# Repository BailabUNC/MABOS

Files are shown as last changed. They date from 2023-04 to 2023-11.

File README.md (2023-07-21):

# MABOS
*All work in the MABOS repository is under Copyright Protections enumerated in the LICENSE file. Please contact Arjun Putcha - arjun22@live.unc.edu - for any questions related to redistribution of this work*

*Please see [fastplotlib](https://github.com/kushalkolar/fastplotlib/tree/master), developed by Kushal Kolar, to learn more about the plotting library we primarily use.

https://github.com/BailabUNC/MABOS/assets/96029511/e3c2583f-f5fd-4558-a8c5-83fa992f67cb

There are three key folders in this repository: full_design, firmware, and application.

## Full Design
This folder contains the *CAD* files (.sch and .brd) detailing schematic and layout of our pulse oximeter. It also contains a CAD library file - COMPONENTS_LIB.flbr - that has the relevant files for each component used in our design.

There is also a folder *Fab_Outputs* that contains the fabrication files necessary for laser cutting the top and bottom side of the board. *_autocad.dxf* files contain the file compatible with our laser cutter. Refer to *protocols/PCB_protocols.pdf* to follow our fabrication process.

Below is the schematic for our Infrared LED and Photodiode drivers; The 5-stage analog signal processing pipeline and led drivers are detailed in the schematic. The same schematic is used for the two other channels.
MABOS Schematic

## Firmware
There are 3 directories in this folder: Arduino, Python, and zephyr_workspace.

### Arduino
Contains the .ino file used for the adafruit_itsybitsy_nrf52840 board. The code allows for the control of 3 LED channels and 3 ADC channels. Currently, the duty cycle is set to 50%, and the acquisition rate at 100 Hz.

We also take a burst sample of each ADC (currently 5 samples) to mitigate some noise, and implement a moving average filter with a window size of 10 samples to smooth the output data.

### Python
The code here will soon be removed.

### Zephyr Workspace
Contains the source code, build files, and modified board files to use the adafruit_itsybitsy_nrf52840 board. The board files are modified to configure 3 LED and 3 ADC channels. You can reference the readme file in *firmware/zephyr_workspace* for further details on modifications made.

## Application
The *utils* folder contains the core API used to acquire, plot, and save biosensor data in real time. The *PPG Widget* python notebook utilizes the core API to operate our device. When running this script, a file named *cache.sqlite3* will be created that contains all acquired data. For our uses, we've found a minute of data acquisition corresponds to ~1 MB of data saved.

The *GUI* folder contains a QT Desktop application used solely for displaying acquired biometrics, including SpO2, Heart Rate, Respiration Rate, and Epidermal Melanin Concentration.

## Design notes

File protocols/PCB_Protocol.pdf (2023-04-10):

1.) Export circuit design (.brd file in Fusion360) as Gerber Zip File

a.

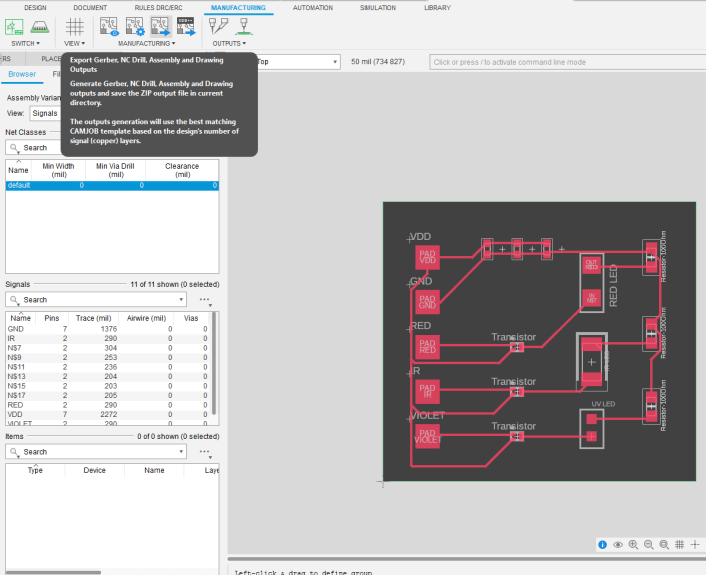
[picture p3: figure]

b. Select “Export Gerber, NC Drill, Assembly, and Drawing Output” output button, and export all files to a .zip file
c. You should see a file named copper_top.gerber in the CAMOutputs folder

i.
2.) Open FlatCAM

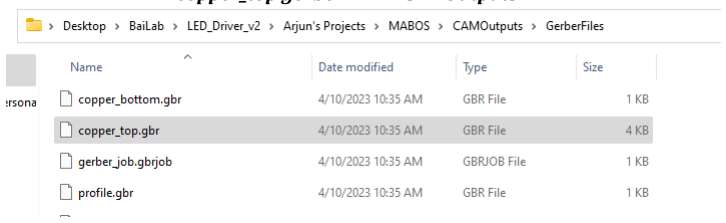
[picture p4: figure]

a. Click ‘File’ and ‘Open Gerber’
b. Navigate to the file you saved above (copper_top.gbr), select said file

c.

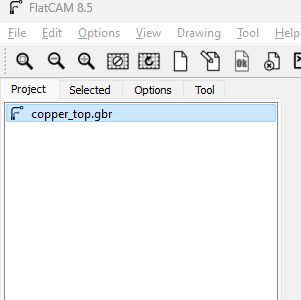
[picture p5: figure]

d. You should see the above file in the project list. Double Click it
e. Modify the parameters as listed below for Total Diameter and Pass Overlap, confirm the resulting design properly traces the counters of each trace be clicking Generate Geometry and visually confirming accuracy, then select File -> Export SVG

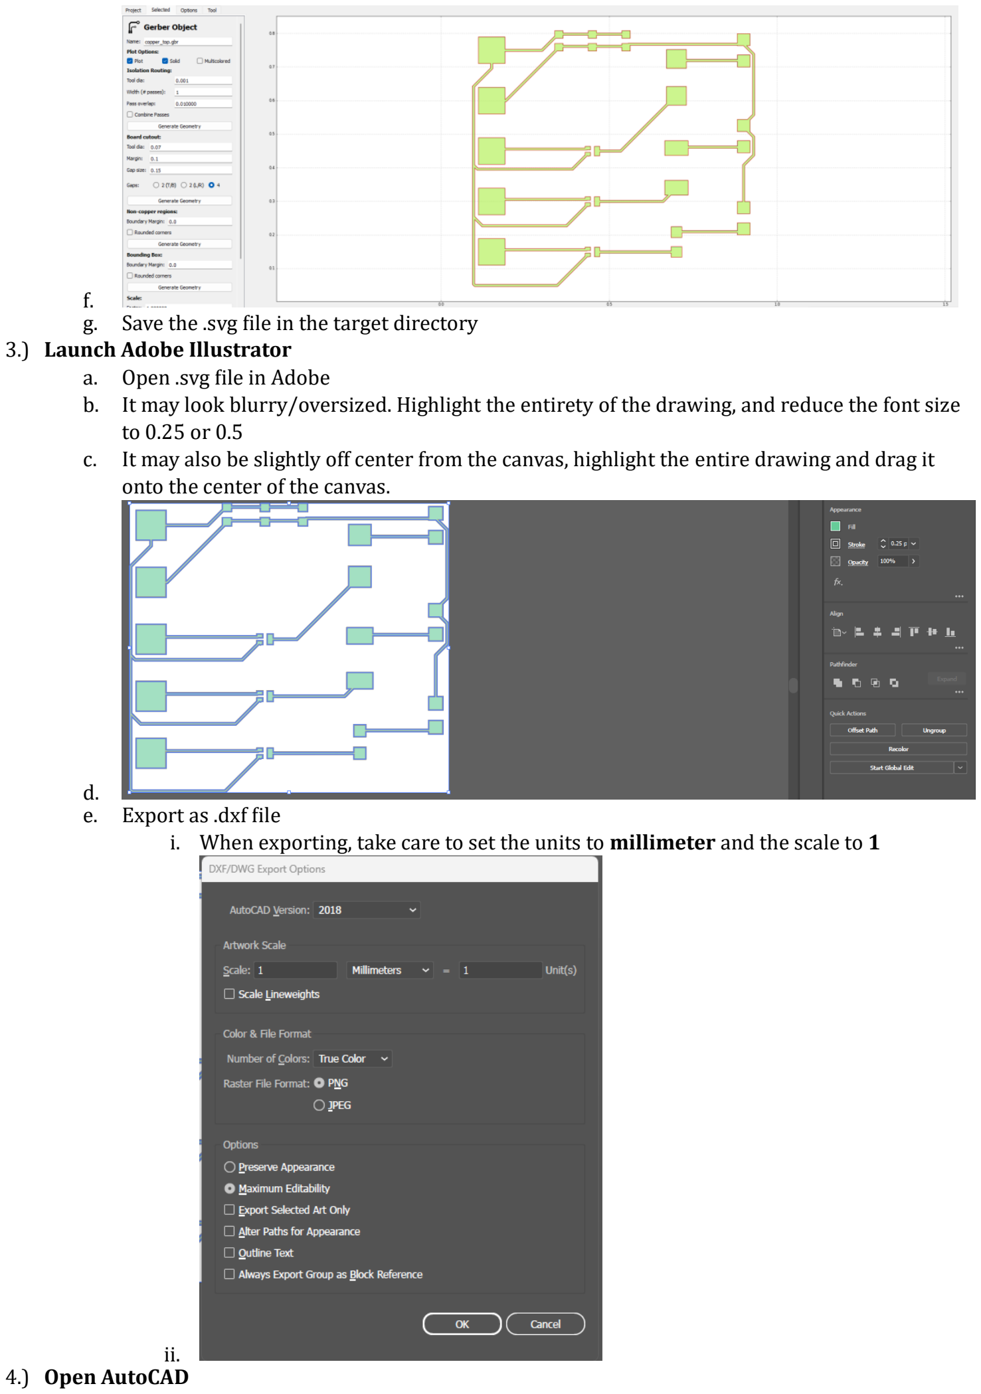
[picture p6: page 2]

f.
g. Save the .svg file in the target directory
3.) Launch Adobe Illustrator
a. Open .svg file in Adobe
b. It may look blurry/oversized. Highlight the entirety of the drawing, and reduce the font size to 0.25 or 0.5
c. It may also be slightly off center from the canvas, highlight the entire drawing and drag it onto the center of the canvas.

d.
e. Export as .dxf file
i. When exporting, take care to set the units to millimeter and the scale to 1

ii.
4.) Open AutoCAD

a. Open the .dxf file

i.

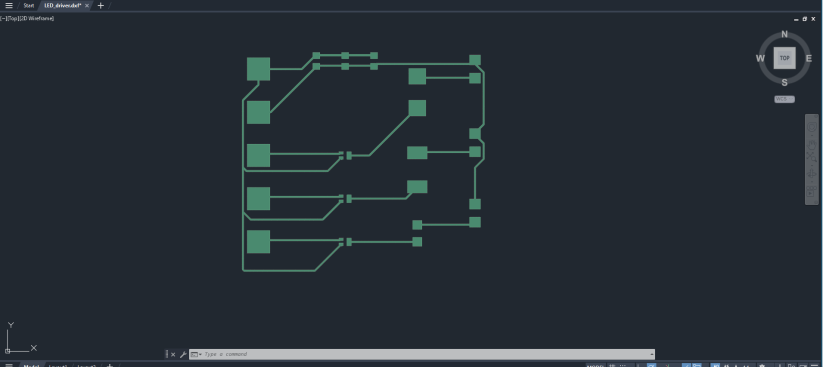
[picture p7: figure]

b. Select the entire circuit, and type X, and you should see the word EXPLODE pop up. Click enter

i.

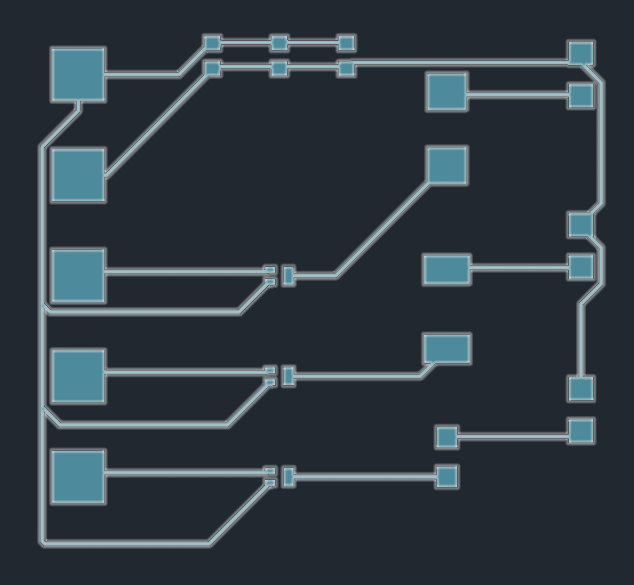
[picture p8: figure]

ii. Repeat this step once more
c. Upon doing step B, you should be able to select individual circuit traces as shown below

i.

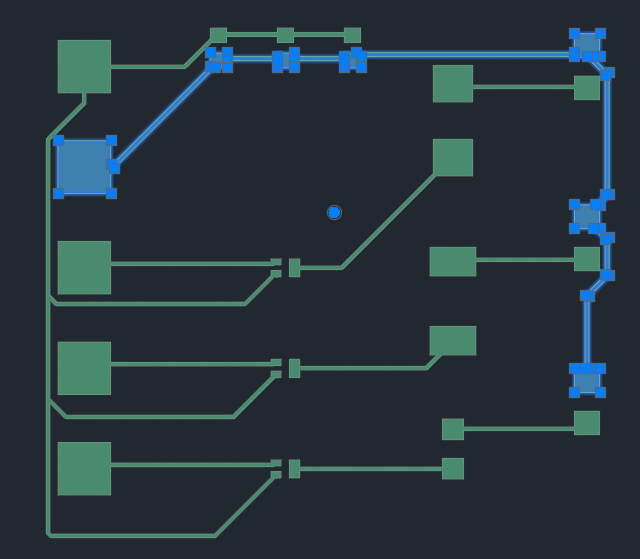
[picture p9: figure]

d. Highlight the entire circuit, type QS and the word Quick Select should pop up. Click enter, the following window will open up:

i.

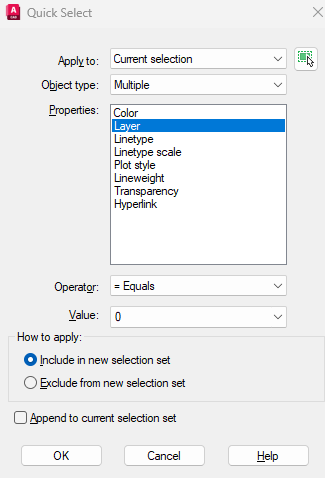
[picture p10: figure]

ii. Set Property to Layer
e. Save the resulting file as a .dxf file, copy this resulting file to a thumbdrive/flashdrive
5.) Launch EZCAD on the desktop associated with the laser printer, plug in the thumbdrive and import the .dxf file
a. File -> Import Vector File -> File_Path.dxf
b. Draw a Rectangle around the entire circuit by selecting Draw Rectangle (yellow square icon on the left vertical bar of the application window).
c. Select the circuit and rectangle elements in the Object List panel, and then click Hatch (the top horizontal bar of the application window, icon looks like an H)
d. Set Hatch Type to the concentric square mode, as shown below, and the Line Space to 0.015, or however small needed to get a good output

e.

f.

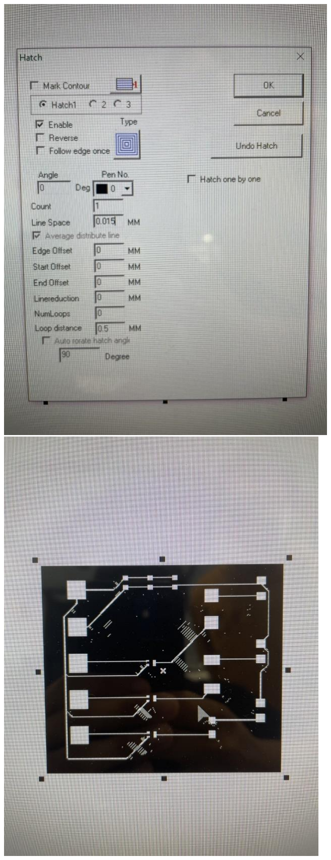
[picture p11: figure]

i. Good output ^
ii. Random ‘shading’ is normal
6.) Laser Cutting Process
a. Take sheet of Copper-FR4, align under the laser.
i. Spray the copper sheet with a thin film of soldermask, dry with pressurized air carefully
b. Make sure the ‘dot’ and ‘line’ of the laser align by adjusting the height of the laser.

c. Select ‘Red’ or ‘Light’ on the bottom of the screen to highlight the area to be cut. Align the copper board appropriately. If you cannot see outline (UV Laser has this issue), place a white tissue above the copper plate. You should now see the outline.
d. Test the settings of the laser
i. For the UV Laser, I used:
1. Loop Count: 1
2. Speed: 1200
3. Current: 0.08
4. Everything else: default ii. For IR Laser, I Used:
1. Power: 30%
2. Loop Count: 1
iii. Cut
7.) Acid Etching
a. Wear PPE
b. Place acid etchant into a rectangular tray, enough to submerge pcb
c. Place pcb within acid using plastic tweezers
d. Start the rocker, leave within for 16 minutes at speed 40
8.) Acetone Wash
a. After acid etching, take pcb out of acid bath using plastic tweezers
b. In a separate, empty, container, use acetone the clean the PCB (hold the pcb with metal tweezers now)
c. Do so until all solder mask has washed off
d. Once done, dispose of all chemicals in chemical waste bin, and clean pcb with water
e. DONE!

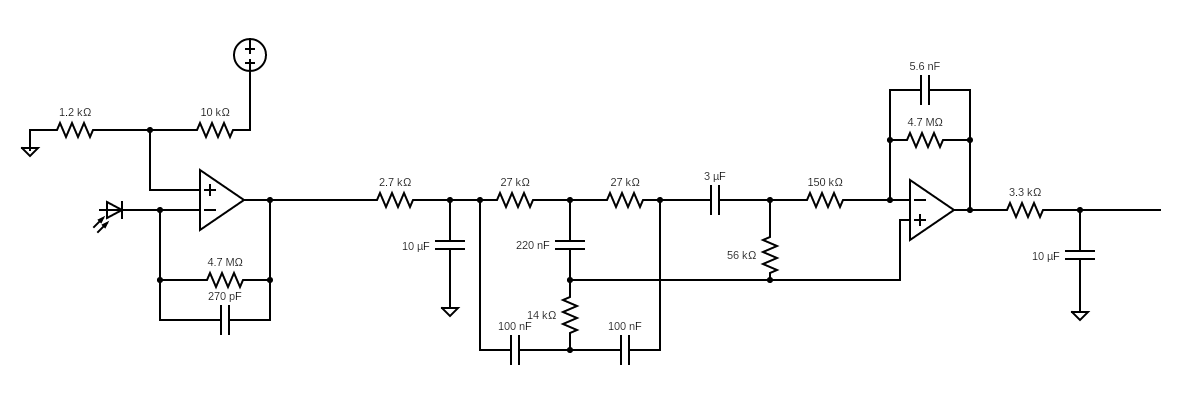
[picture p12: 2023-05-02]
protocols/Filter_Amplification_PD_Schematic.png

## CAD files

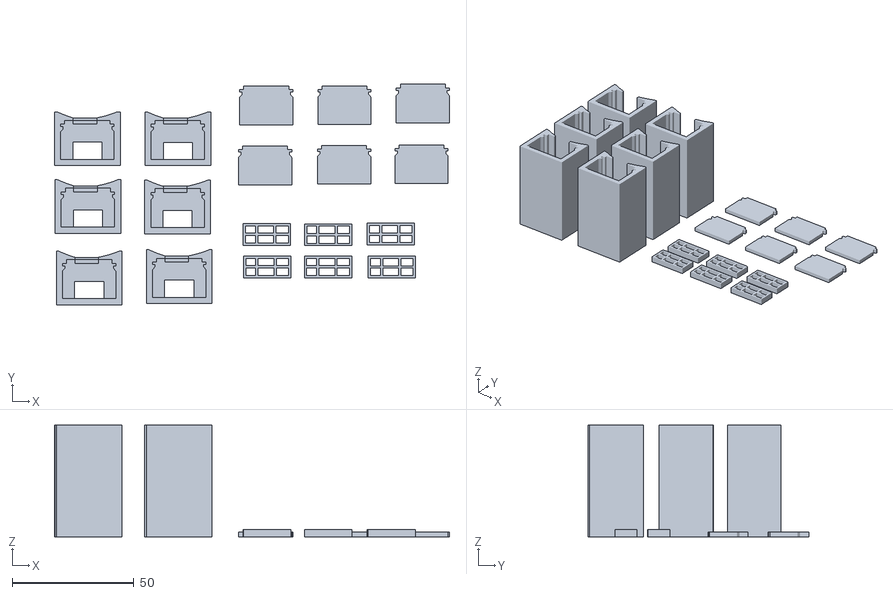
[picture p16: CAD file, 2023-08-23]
full_design/casing/six_full_casings.stl
162.1 x 90.5 x 45.8

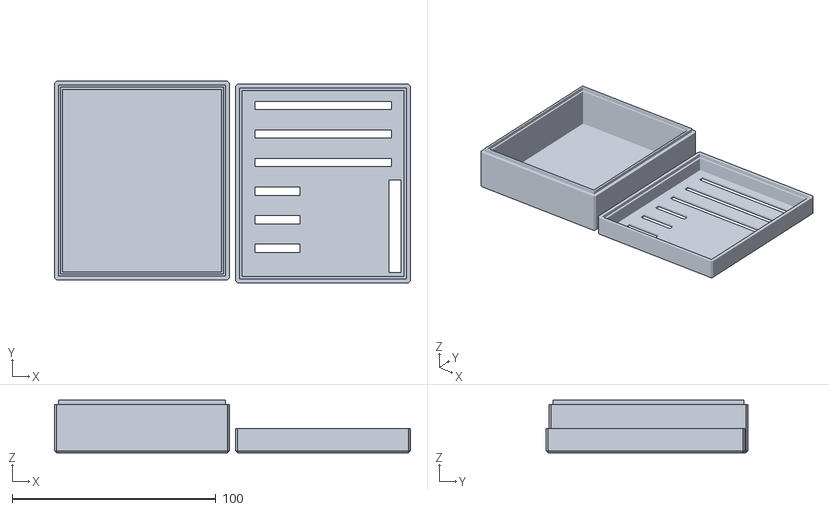
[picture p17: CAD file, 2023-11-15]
full_design/casing/modular_case_design.stl
174.7 x 99.0 x 26.0

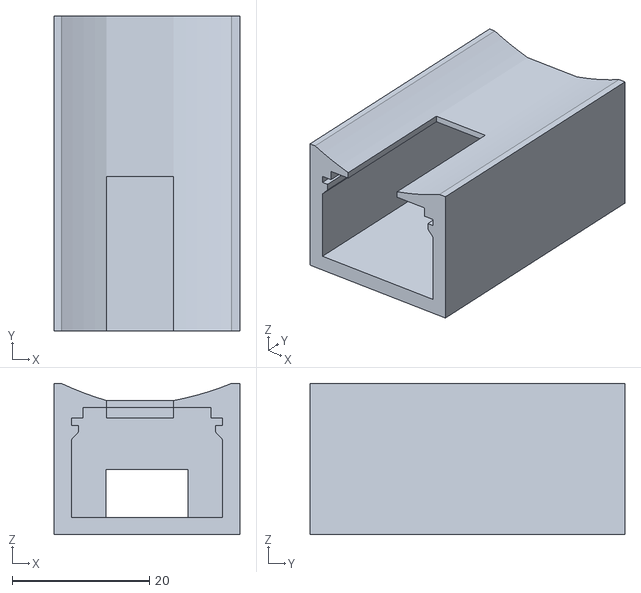
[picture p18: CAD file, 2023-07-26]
full_design/casing/primary_case_design.stl
27.0 x 45.8 x 22.0

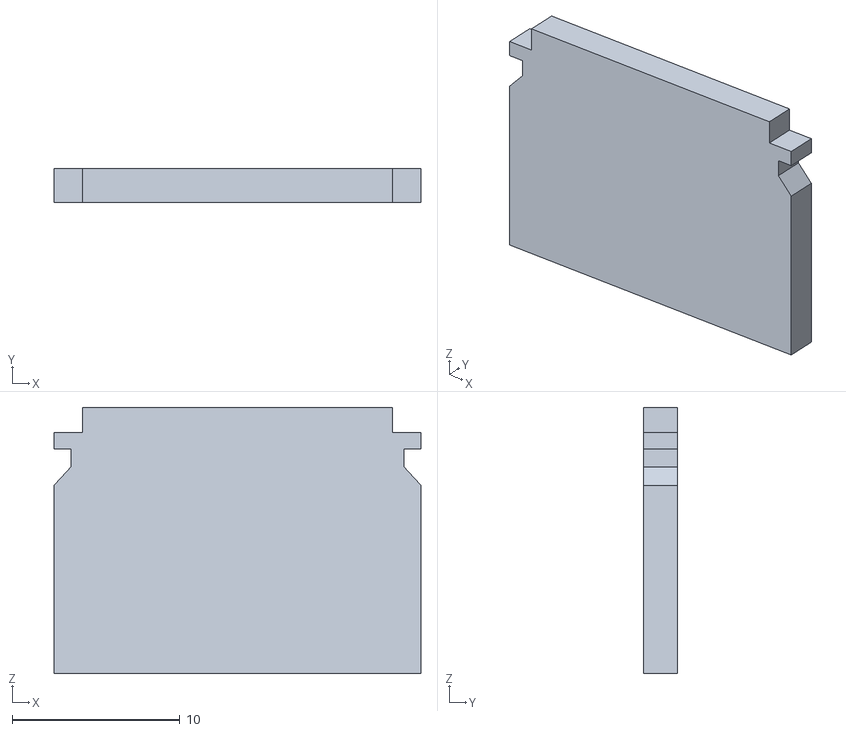
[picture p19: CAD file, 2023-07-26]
full_design/casing/primary_case_plug.stl
21.9 x 2.00 x 15.9

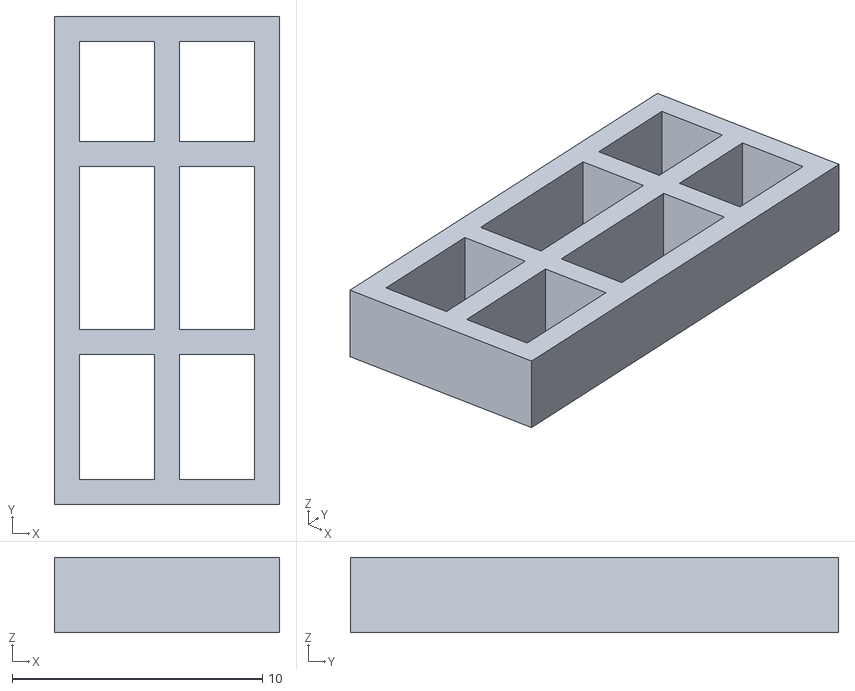
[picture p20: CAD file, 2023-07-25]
full_design/casing/light_blocker.stl
9.00 x 19.5 x 3.00

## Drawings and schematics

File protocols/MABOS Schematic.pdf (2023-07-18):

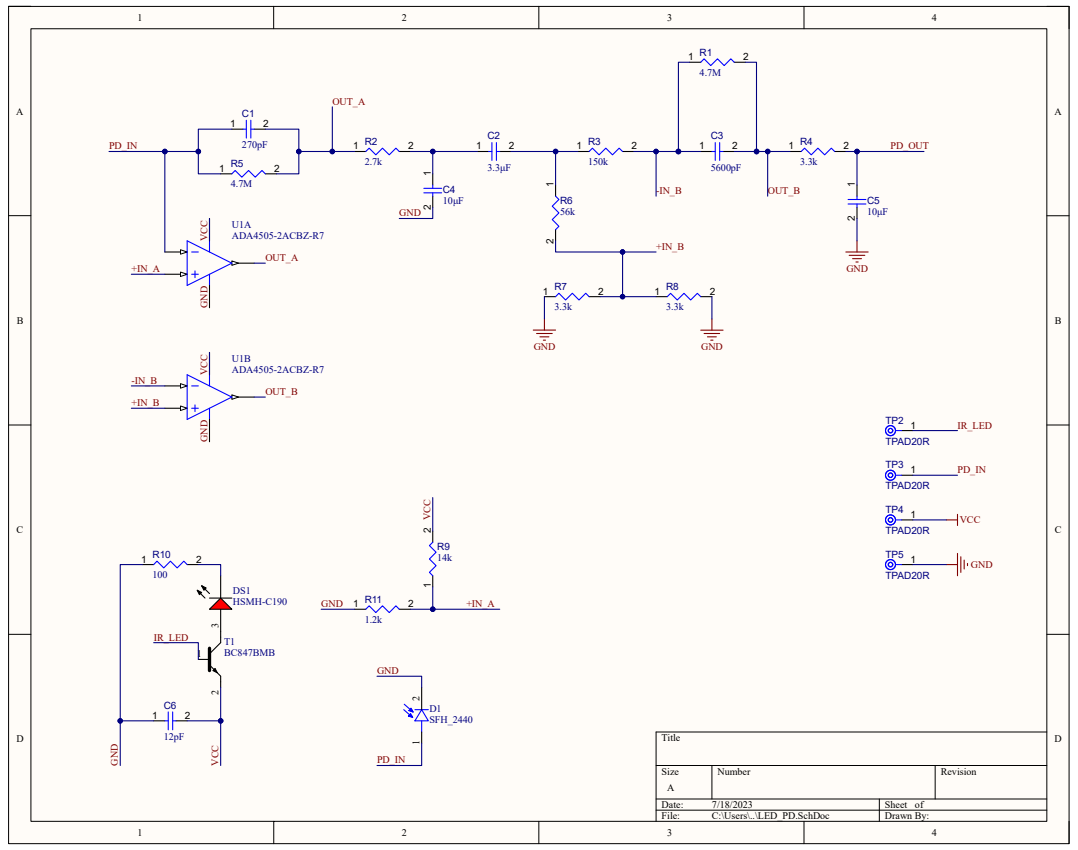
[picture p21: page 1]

VCC VCC GND GND

Size A | Number | Revision

Date: 7/18/2023 | Sheet of
File: C:\Users\..\LED_PD.SchDoc | Drawn By:

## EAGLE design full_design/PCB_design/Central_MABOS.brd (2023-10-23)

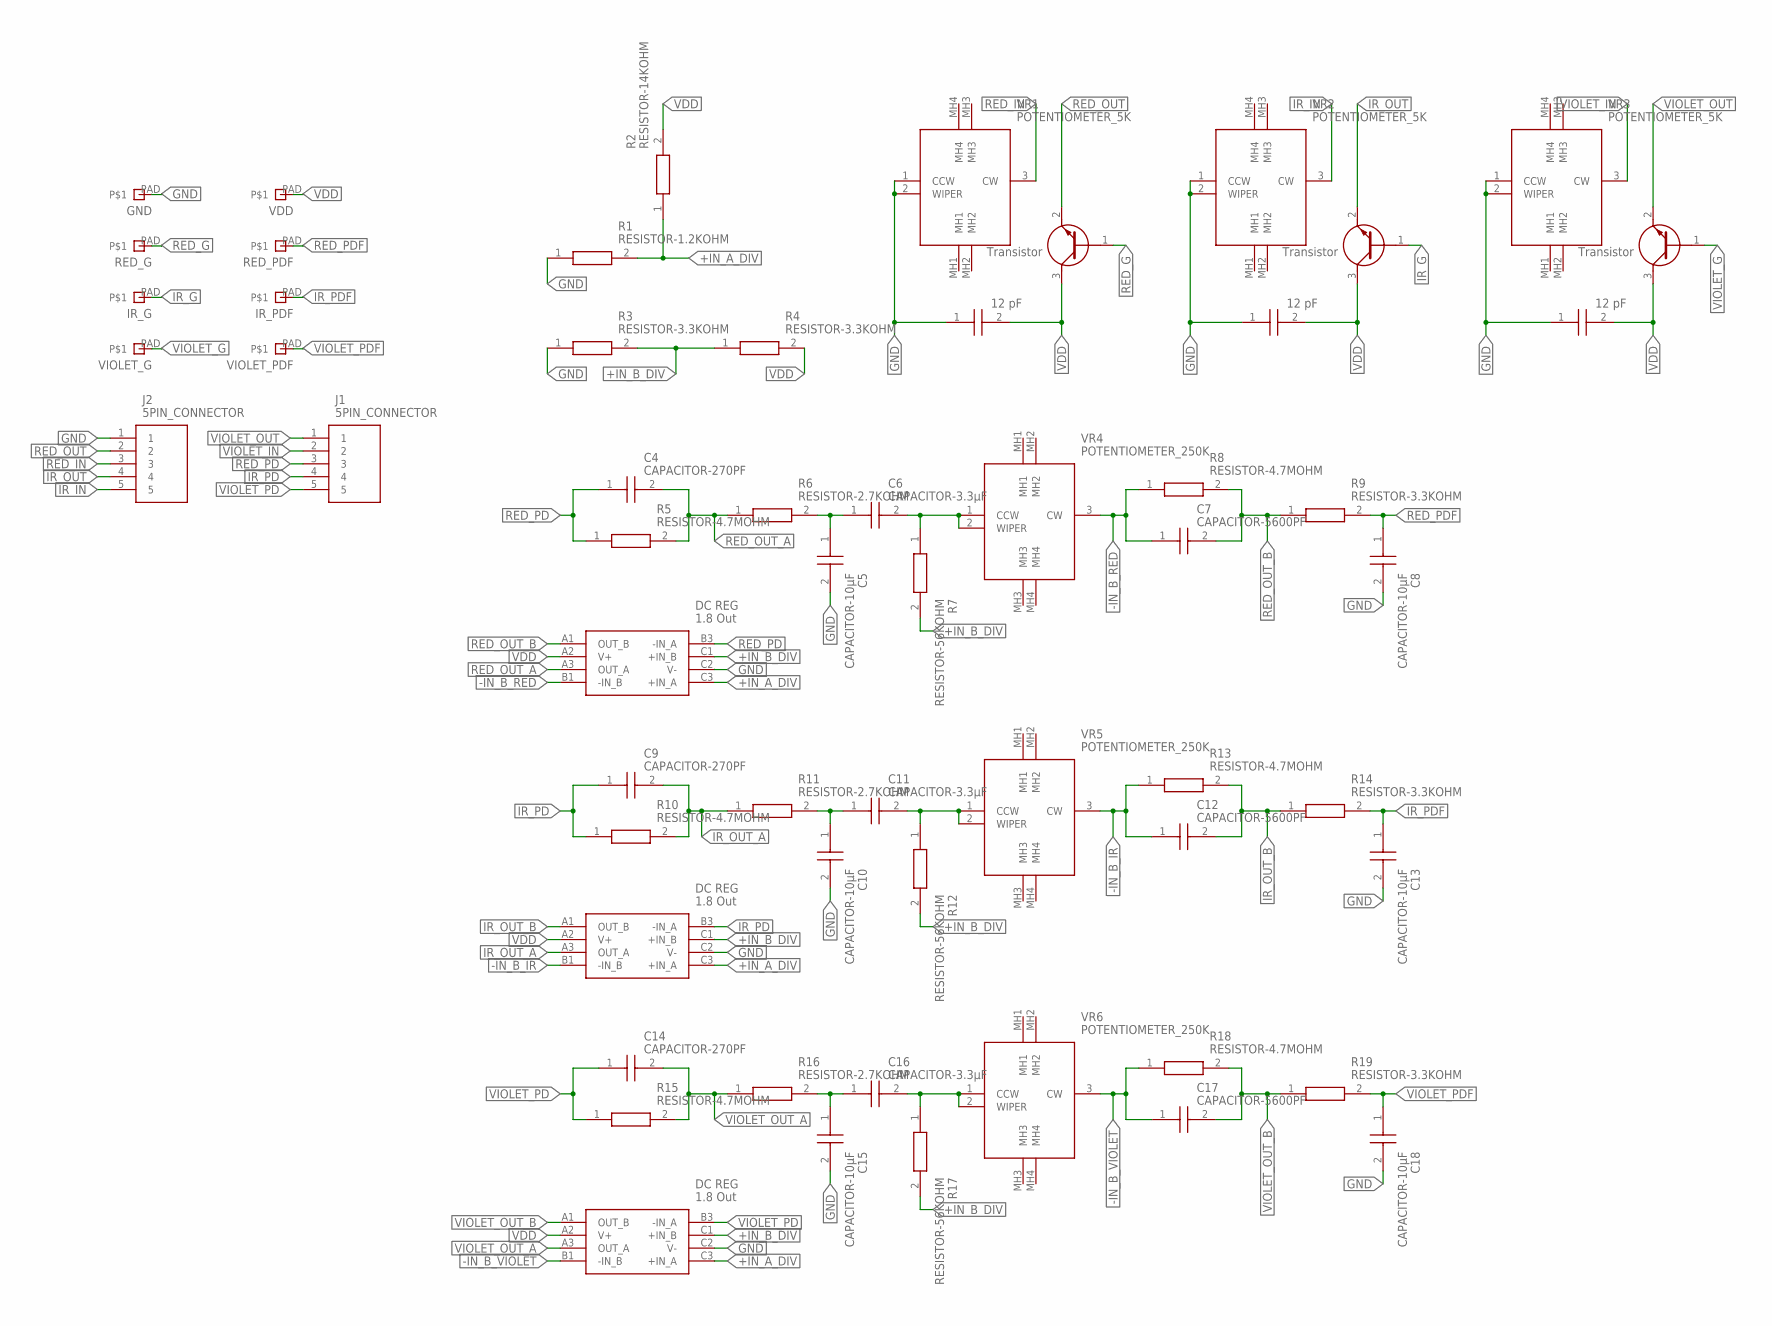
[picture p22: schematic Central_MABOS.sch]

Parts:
C1, C2, C3: CAPACITOR-12PF; CAPC1005X55N
C4, C9, C14: CAPACITOR-270PF; CAPC1005X55N
C5, C8, C10, C13, C15, C18: CAPACITOR-10µF; C0402
C6, C11, C16: CAPACITOR-3.3µF; C0402
C7, C12, C17: CAPACITOR-5600PF; CAPC1005X55N
GND: PAD
IC1, IC2, IC3: ADA4505-2; BGA8C50P3X3_142X142X65
IR_G: PAD
IR_PDF: PAD
J1, J2: 5PIN_CONNECTOR; SHDR5W114P0X419_1X5_2228X658X1
Q1, Q2, Q3: TRANSISTOR; SOT883B
R1: RESISTOR-1.2KOHM; ERJPA2_(0402)
R2: RESISTOR-14KOHM; ERJ2RKD1004X
R3, R4, R9, R14, R19: RESISTOR-3.3KOHM; ERJPA2_(0402)
R5, R8, R10, R13, R15, R18: RESISTOR-4.7MOHM; ERJ2RKD1004X
R6, R11, R16: RESISTOR-2.7KOHM; ERJPA2_(0402)
R7, R12, R17: RESISTOR-56KOHM; ERJ2RKD1004X
RED_G: PAD
RED_PDF: PAD
VDD: PAD
VIOLET_G: PAD
VIOLET_PDF: PAD
VR1, VR2, VR3: POTENTIOMETER_5K; POTENTIOMETER
VR4, VR5, VR6: POTENTIOMETER_250K; PTA60432015DPB254

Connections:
+IN_A_DIV: IC1.C3 (+IN_A), IC2.C3 (+IN_A), IC3.C3 (+IN_A), R1.2, R2.1
+IN_B_DIV: IC1.C1 (+IN_B), IC2.C1 (+IN_B), IC3.C1 (+IN_B), R3.2, R4.1, R7.2, R12.2, R17.2
-IN_B_IR: C12.1, IC2.B1 (-IN_B), R13.1, VR5.3 (CW)
-IN_B_RED: C7.1, IC1.B1 (-IN_B), R8.1, VR4.3 (CW)
-IN_B_VIOLET: C17.1, IC3.B1 (-IN_B), R18.1, VR6.3 (CW)
GND: C1.1, C2.1, C3.1, C5.2, C8.2, C10.2, C13.2, C15.2, C18.2, GND.PAD, IC1.C2 (V-), IC2.C2 (V-), IC3.C2 (V-), J2.1, R1.1, R3.1, VR1.1 (CCW), VR1.2 (WIPER), VR2.1 (CCW), VR2.2 (WIPER), VR3.1 (CCW), VR3.2 (WIPER)
IR_G: IR_G.PAD, Q2.1 (B)
IR_IN: J2.5, VR2.3 (CW)
IR_OUT: J2.4, Q2.2 (E)
IR_OUT_A: C9.2, IC2.A3 (OUT_A), R10.2, R11.1
IR_OUT_B: C12.2, IC2.A1 (OUT_B), R13.2, R14.1
IR_PD: C9.1, IC2.B3 (-IN_A), J1.4, R10.1
IR_PDF: C13.1, IR_PDF.PAD, R14.2
unnamed: C5.1, C6.1, R6.2
unnamed: C6.2, R7.1, VR4.1 (CCW), VR4.2 (WIPER)
unnamed: C10.1, C11.1, R11.2
unnamed: C11.2, R12.1, VR5.1 (CCW), VR5.2 (WIPER)
unnamed: C15.1, C16.1, R16.2
unnamed: C16.2, R17.1, VR6.1 (CCW), VR6.2 (WIPER)
RED_G: Q1.1 (B), RED_G.PAD
RED_IN: J2.3, VR1.3 (CW)
RED_OUT: J2.2, Q1.2 (E)
RED_OUT_A: C4.2, IC1.A3 (OUT_A), R5.2, R6.1
RED_OUT_B: C7.2, IC1.A1 (OUT_B), R8.2, R9.1
RED_PD: C4.1, IC1.B3 (-IN_A), J1.3, R5.1
RED_PDF: C8.1, R9.2, RED_PDF.PAD
VDD: C1.2, C2.2, C3.2, IC1.A2 (V+), IC2.A2 (V+), IC3.A2 (V+), Q1.3 (C), Q2.3 (C), Q3.3 (C), R2.2, R4.2, VDD.PAD
VIOLET_G: Q3.1 (B), VIOLET_G.PAD
VIOLET_IN: J1.2, VR3.3 (CW)
VIOLET_OUT: J1.1, Q3.2 (E)
VIOLET_OUT_A: C14.2, IC3.A3 (OUT_A), R15.2, R16.1
VIOLET_OUT_B: C17.2, IC3.A1 (OUT_B), R18.2, R19.1
VIOLET_PD: C14.1, IC3.B3 (-IN_A), J1.5, R15.1
VIOLET_PDF: C18.1, R19.2, VIOLET_PDF.PAD

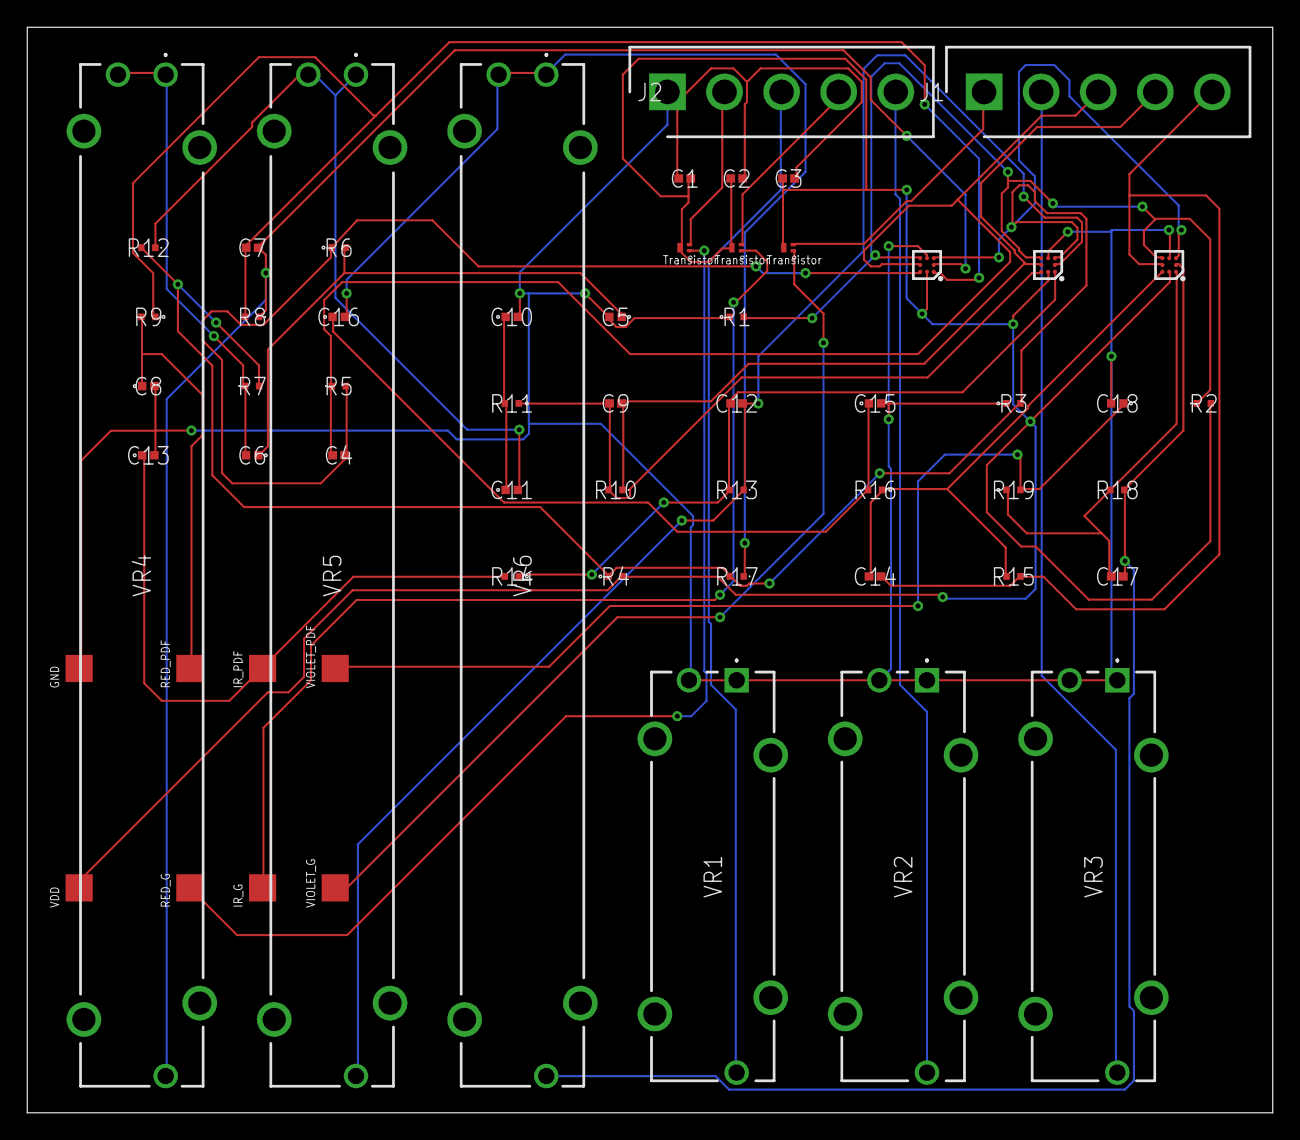
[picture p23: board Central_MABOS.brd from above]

Board: 2 copper layers, 91.4 x 79.7 mm, 59 parts (0 on the bottom side), 34 nets.

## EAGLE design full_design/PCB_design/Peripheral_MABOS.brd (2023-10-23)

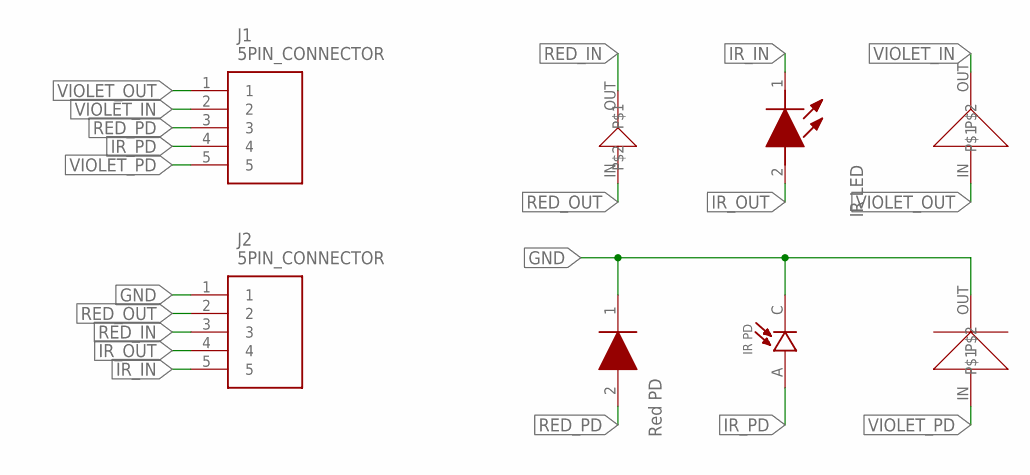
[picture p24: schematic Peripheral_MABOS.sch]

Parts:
D1: REDPD; SFH2713
D2: IRPD; XDCR_VEMD2023X01
J1, J2: 5PIN_CONNECTOR; SHDR5W114P0X419_1X5_2228X658X1
LED1: IRLED; LEDC3216X180N
U$1: REDLED
U$2: UVLED
U$3: UVPD

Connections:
GND: D1.1 (K), D2.C, J2.1, U$3.OUT
IR_IN: J2.5, LED1.1 (K)
IR_OUT: J2.4, LED1.2 (A)
IR_PD: D2.A, J1.4
RED_IN: J2.3, U$1.OUT
RED_OUT: J2.2, U$1.IN
RED_PD: D1.2 (A), J1.3
VIOLET_IN: J1.2, U$2.OUT
VIOLET_OUT: J1.1, U$2.IN
VIOLET_PD: J1.5, U$3.IN

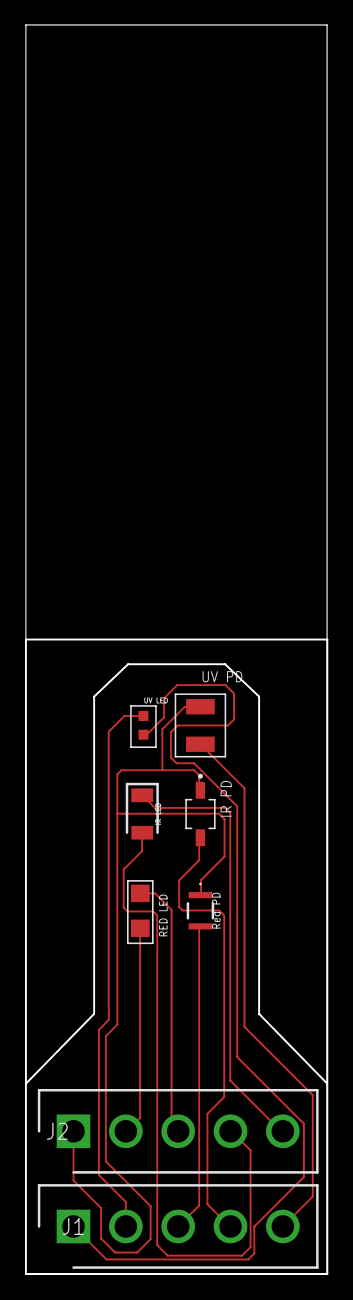
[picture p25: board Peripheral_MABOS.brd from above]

Board: 2 copper layers, 24.1 x 100.0 mm, 8 parts (0 on the bottom side), 10 nets.

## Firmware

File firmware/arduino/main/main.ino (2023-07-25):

#include <Arduino.h>
#include <Adafruit_TinyUSB.h> // for Serial

// Pin values for led/pd
#define red_led 7
#define ir_led 12
#define violet_led 10
#define red_adc A4
#define ir_adc A0
#define violet_adc A2
// Set flags for red, ir, violet
#define red 0
#define ir 1
#define violet 2
// constants for adjusting ADC input
float MV_PER_LSB (0.73242188F); // 3.0V ADC range and 12-bit ADC resolution = 3000mV/4096
#define VBAT_DIVIDER (0.5F)
#define VBAT_DIVIDER_COMP (2.0F)
#define REAL_VBAT_MV_PER_LSB (VBAT_DIVIDER_COMP * MV_PER_LSB)
float raw;
// constants for burst & moving average filter
#define sampleSize 5    // number of samples for burst filter
#define sampleRate 100 //in Hz
#define window_size 10  // Number of samples for moving average filter
int red_idx = 0;       
int ir_idx = 0;
int violet_idx = 0;     // index of moving average filter to replace
int burst_sum = 0;
int burst_avg = 0;
// variables for managing adc processing
int red_sum = 0;
int ir_sum = 0;
int violet_sum = 0;
int red_avg;
int ir_avg;
int violet_avg;
int red_adc_arr[window_size];
int ir_adc_arr[window_size];
int violet_adc_arr[window_size];
// keys for associating flag with adc channel and led channel
int adc_key[3] = {red_adc, ir_adc, violet_adc};
int led_key[3] = {red_led, ir_led, violet_led};
int channel_flag = 0;
int avg;
int channel_data[3];


float readADC(int channel_flag){
    raw = analogRead(adc_key[channel_flag]);
    return raw*REAL_VBAT_MV_PER_LSB;
}

void setup() {
  // Set up LEDs
  pinMode(red_led, OUTPUT);
  pinMode(ir_led, OUTPUT);
  pinMode(violet_led, OUTPUT);
  // define baudrate
  Serial.begin(115200);
  while ( !Serial ) delay(10);
  // Setup ADC channels
  analogReference(AR_INTERNAL_3_0);
  analogReadResolution(12);
  delay(1);
  // Read all three adc channels
  readADC(red_adc);
  readADC(ir_adc);
  readADC(violet_adc);
}

float burst_sample(int channel_flag) {
  for (int i=0; i<sampleSize; i++){
      burst_sum += readADC(channel_flag);
      delay(1000/(6*sampleRate*sampleSize));
    }
  burst_avg = burst_sum/sampleSize;
  burst_sum = 0;
  return burst_avg;
}

float moving_average_filter(int channel_flag, int burst_val) {
  if (channel_flag == red) {
    red_sum = red_sum - red_adc_arr[red_idx];
    red_adc_arr[red_idx] = burst_val;
    red_sum += burst_val;
    red_avg = red_sum/window_size;
    red_idx = (red_idx+1) % window_size;
    return red_avg;
  }
  else if (channel_flag == ir) {
    ir_sum = ir_sum - ir_adc_arr[ir_idx];
    ir_adc_arr[ir_idx] = burst_val;
    ir_sum += burst_val;
    ir_avg = ir_sum/window_size;
    ir_idx = (ir_idx+1) % window_size;
    return ir_avg;
  }
  else {
    violet_sum = violet_sum - violet_adc_arr[violet_idx];
    violet_adc_arr[violet_idx] = burst_val;
    violet_sum += burst_val;
    violet_avg = violet_sum/window_size;
    violet_idx = (violet_idx+1) % window_size;
    return violet_avg;
  }
}

float channel_acquisition(int channel_flag) {
  digitalWrite(led_key[channel_flag], HIGH);
  avg = moving_average_filter(channel_flag, burst_sample(channel_flag));
  digitalWrite(led_key[channel_flag], LOW);
  return avg;
}

void loop() {

    channel_flag = red;
    channel_data[red] = channel_acquisition(channel_flag);
    delay(1000/(6*sampleRate));
    channel_flag = ir;
    channel_data[ir] = channel_acquisition(channel_flag);
    delay(1000/(6*sampleRate));
    channel_flag = violet;
    channel_data[violet] = channel_acquisition(channel_flag);
    delay(1000/(6*sampleRate));
  
    Serial.println(channel_data[red]);
    Serial.println(channel_data[ir]);
    Serial.println(channel_data[violet]);
    Serial.flush();


}

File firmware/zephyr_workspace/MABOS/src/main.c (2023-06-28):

/*
 * Copyright (c) 2016 Intel Corporation
 *
 * SPDX-License-Identifier: Apache-2.0
 */
#include <inttypes.h>
#include <stddef.h>
#include <stdint.h>
#include <string.h>
#include <stdio.h>

#include <zephyr/sys/printk.h>
#include <zephyr/sys/util.h>
#include <zephyr/logging/log.h>

#include <zephyr/kernel.h>
#include <zephyr/drivers/uart.h>
#include <zephyr/drivers/gpio.h>
#include <zephyr/drivers/adc.h>
#include <zephyr/device.h>
#include <zephyr/devicetree.h>

/* 1000 msec = 1 sec */
#define SLEEP_TIME_MS   1000

/* The devicetree node identifier for the "led0" - "led2" aliases. */
#define LED0_NODE DT_ALIAS(led0)
#define LED1_NODE DT_ALIAS(led1)
#define LED2_NODE DT_ALIAS(led2)

static const struct gpio_dt_spec led0 = GPIO_DT_SPEC_GET(LED0_NODE, gpios);
static const struct gpio_dt_spec led1 = GPIO_DT_SPEC_GET(LED1_NODE, gpios);
static const struct gpio_dt_spec led2 = GPIO_DT_SPEC_GET(LED2_NODE, gpios);

#define DT_SPEC_AND_COMMA(node_id, prop, idx) \
	ADC_DT_SPEC_GET_BY_IDX(node_id, idx),

/* Data of ADC io-channels specified in devicetree. */
static const struct adc_dt_spec adc_channels[] = {
	DT_FOREACH_PROP_ELEM(DT_PATH(zephyr_user), io_channels,
			     DT_SPEC_AND_COMMA)
};

/* Setup UART device. In devicetree file uart0 is only option */
static const struct device *uart0 = DEVICE_DT_GET(DT_NODELABEL(uart0));
struct uart_config uart_cfg = {
	.baudrate = 115200,
	.parity = UART_CFG_PARITY_NONE,
	.stop_bits = UART_CFG_STOP_BITS_1,
	.flow_ctrl = UART_CFG_FLOW_CTRL_NONE,
	.data_bits = UART_CFG_DATA_BITS_8,
};

void send_str(const struct device *uart, char *str)
{
	int msg_len = strlen(str);

	for (int i = 0; i < msg_len; i++) {
		uart_poll_out(uart, str[i]);
	}

	printk("Device %s sent: \"%s\"\n", uart->name, str);
}

int main(void)
{
	if (!gpio_is_ready_dt(&led0) || !gpio_is_ready_dt(&led1) || !gpio_is_ready_dt(&led2)) {
		return 0;
	}

	int ret0 = gpio_pin_configure_dt(&led0, GPIO_OUTPUT_ACTIVE);
        int ret1 = gpio_pin_configure_dt(&led1, GPIO_OUTPUT_ACTIVE);
        int ret2 = gpio_pin_configure_dt(&led2, GPIO_OUTPUT_ACTIVE);

	if (ret0 || ret1 || ret2 < 0) {
		return 0;
	}

        int err;
	uint32_t count = 0;
	uint16_t buf;
	struct adc_sequence sequence = {
		.buffer = &buf,
		/* buffer size in bytes, not number of samples */
		.buffer_size = sizeof(buf),
	};

	/* Configure channels individually prior to sampling. */
	for (size_t i = 0U; i < ARRAY_SIZE(adc_channels); i++) {
		if (!device_is_ready(adc_channels[i].dev)) {
			printk("ADC controller device %s not ready\n", adc_channels[i].dev->name);
			return 0;
		}

		err = adc_channel_setup_dt(&adc_channels[i]);
		if (err < 0) {
			printk("Could not setup channel #%d (%d)\n", i, err);
			return 0;
		}
	}

        /* Configure UART channel */
        int rc;
	char send_buf[64];
	rc = uart_configure(uart0, &uart_cfg);
	if (rc) {
		printk("Could not configure device %s", uart0->name);
	}

	while (1) {
                printk("ADC reading[%u]:\n", count++);
                snprintf(send_buf, 64, "Hello from device %s, num %d", uart0->name, count);
                send_str(uart0, send_buf);
                // Toggle LEDs
		//gpio_pin_toggle_dt(&led0);
  //              gpio_pin_toggle_dt(&led1);
  //              gpio_pin_toggle_dt(&led2);

                //  k_msleep(SLEEP_TIME_MS/2);
                int32_t val_mv;

                gpio_pin_toggle_dt(&led0);
                k_msleep(SLEEP_TIME_MS/2);
                (void)adc_sequence_init_dt(&adc_channels[0], &sequence);
                adc_read(adc_channels[0].dev, &sequence);

                if (adc_channels[0].channel_cfg.differential) {
                    val_mv = (int32_t)((int16_t)buf);
                } else {
                    val_mv = (int32_t)buf;
                }
                printk("%"PRId32, val_mv);
                err = adc_raw_to_millivolts_dt(&adc_channels[0],
						       &val_mv);
                printk(" = %"PRId32" mV\n", val_mv);

                gpio_pin_toggle_dt(&led0);
                gpio_pin_toggle_dt(&led1);
                k_msleep(SLEEP_TIME_MS/2);
                (void)adc_sequence_init_dt(&adc_channels[0], &sequence);
                adc_read(adc_channels[0].dev, &sequence);

                if (adc_channels[0].channel_cfg.differential) {
                    val_mv = (int32_t)((int16_t)buf);
                } else {
                    val_mv = (int32_t)buf;
                }
                printk("%"PRId32, val_mv);
                err = adc_raw_to_millivolts_dt(&adc_channels[0],
						       &val_mv);
                printk(" = %"PRId32" mV\n", val_mv);

                gpio_pin_toggle_dt(&led1);
                gpio_pin_toggle_dt(&led2);
                k_msleep(SLEEP_TIME_MS/2);
                (void)adc_sequence_init_dt(&adc_channels[0], &sequence);
                adc_read(adc_channels[0].dev, &sequence);

                if (adc_channels[0].channel_cfg.differential) {
                    val_mv = (int32_t)((int16_t)buf);
                } else {
                    val_mv = (int32_t)buf;
                }
                printk("%"PRId32, val_mv);
                err = adc_raw_to_millivolts_dt(&adc_channels[0],
						       &val_mv);
                printk(" = %"PRId32" mV\n", val_mv);
                gpio_pin_toggle_dt(&led2);
  //              for (size_t i = 0U; i < ARRAY_SIZE(adc_channels); i++) {
		//	int32_t val_mv;

		//	printk("- %s, channel %d: ",
		//	       adc_channels[i].dev->name,
		//	       adc_channels[i].channel_id);

		//	(void)adc_sequence_init_dt(&adc_channels[i], &sequence);

		//	err = adc_read(adc_channels[i].dev, &sequence);
		//	if (err < 0) {
		//		printk("Could not read (%d)\n", err);
		//		continue;
		//	}

		//	/*
		//	 * If using differential mode, the 16 bit value
		//	 * in the ADC sample buffer should be a signed 2's
		//	 * complement value.
		//	 */
		//	if (adc_channels[i].channel_cfg.differential) {
		//		val_mv = (int32_t)((int16_t)buf);
		//	} else {
		//		val_mv = (int32_t)buf;
		//	}
		//	printk("%"PRId32, val_mv);
		//	err = adc_raw_to_millivolts_dt(&adc_channels[i],
		//				       &val_mv);
		//	/* conversion to mV may not be supported, skip if not */
		//	if (err < 0) {
		//		printk(" (value in mV not available)\n");
		//	} else {
		//		printk(" = %"PRId32" mV\n", val_mv);
		//	}
		//}
		//k_msleep(SLEEP_TIME_MS/2);
	}
	return 0;
}

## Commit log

2023-04-10 LED_Driver Module added
    [LED_Driver.brd, LED_Driver.f3z, LED_Driver.sch, Laser_Cut_File.dxf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]
2023-04-12 Add module test for PD filter/amp circuit on breadboard. Will upload schematic of filtering circuit later
    [PD_breadboard.brd, PD_breadboard.f3z, PD_breadboard.sch, PD_breadboard_autocad.dxf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]
2023-04-21 LED-PD module test
    [LED_PD_Breadboard.brd, LED_PD_Breadboard.f3z, LED_PD_Breadboard.sch, LED_PD_breadboard.dxf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]
2023-05-02 Schematic of filtering circuit
2023-05-04 updated components library. Added schematic for filter/amp circuit
2023-05-05 Add schematic & layout for filter_amplification circuit
    [PD_Filter_Amp.f3z, PD_Filter_Amp_illustrator.dxf, copper_bottom.gbr, copper_top.gbr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]
2023-05-05 reorganize module_tests folder
    [LED_PD_breadboard.dxf, LED_PD_breadboard_autocad.dxf, Laser_Cut_File.dxf, PD_Filter_Amp.f3z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]
2023-05-08 modified filter/amp circuit fab
    [PD_Filter_Amp_illustrator.dxf, copper_top.gbr, drill_1_16.xln, gerber_job.gbrjob]
2023-05-09 fixed bug in filter circuit, added test points between each stage
    [PD_Filter_Amp.brd, PD_Filter_Amp.f3z, PD_Filter_Amp.sch, PD_Filter_Amp_illustrator.dxf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]
2023-05-15 led pd full circuit
    [Red_LED_PD.brd, Red_LED_PD.f3z, Red_LED_PD.sch]
2023-05-16 fabrication files for led-pd full circuit
    [LED_PD_full.dxf, copper_bottom.gbr, copper_top.gbr, drill_1_16.xln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]
2023-05-29 arduino base firmware code
2023-05-30 reformat arduino folder
2023-05-30 initial attempt at moving average filter with burst sampling
2023-05-30 adding burst sampling and moving average filter
2023-06-01 schematic and layout for full oximeter
    [copper_bottom.gbr, copper_top.gbr, drill_1_16.xln, full_design.brd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]
2023-06-01 fabrication files for top/bottom of pcb?
2023-06-09 modify firmware to handle 3 channels, 100 Hz, 50% duty cycle
2023-06-29 move module tests to resources repo
    [LED_Driver.brd, LED_Driver.f3z, LED_Driver.sch, LED_PD_Breadboard.brd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]
2023-07-18 updates to schematic docs
    [3_Channel_MABOS.f3d]
2023-07-25 change LED pin output
2023-07-25 3d print file for light blocker
    [light_blocker.stl]
2023-07-26 updated file names
    [case_design.stl, case_plug.stl]
2023-08-01 Update library files
    [copper_bottom.gbr, copper_top.gbr, drill_1_16.xln, gerber_job.gbrjob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]
2023-08-23 added 3D printing file for full casing
    [six_full_casings.stl]
2023-10-19 update component libraries to include connector and rheostat
2023-10-23 switch to modular design of mabos. central handles ASP and addes rheometer for LED brightness and ASP gain control. Peripheral has LED/PD array
    [3_Channel_MABOS.f3d, Central_MABOS.brd, Central_MABOS.sch, Peripheral_MABOS.brd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]
2023-11-15 modified filenames and updated casing design
    [Central_MABOS.brd, Central_MABOS.sch, Peripheral_MABOS.brd, Peripheral_MABOS.sch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]
